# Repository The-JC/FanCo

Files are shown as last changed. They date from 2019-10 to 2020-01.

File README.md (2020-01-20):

# FanCo
  
FanCo is an advanced wind tunnel fan controller. Monitoring and regulating up to 120 fans individually with its custom UI or the API. 
The UI navigation is simple and intuitive utilizing just a rotary encoder.
FanCo is also capable of logging fan speeds over a longer period for later analyzation. 

FanCo is made up of two fundamental components. The master managing the UI and logging. And second, the slave, measuring actual speeds and compensate fluctuations in speed. Each Slave is capable of regulating up to 4 fans. Further slaves can be connected via cables to expand the maximum amounts of fans and also remove the number of control cables needed. 

## Table of contents
- [Requirements](#Requirements)
- [Installation](#Installation)
- [Usage](#Usage)
- [Principle of operation](#Principle%20of%20operation)
- [Troubleshooting](#Troubleshooting)
- [ToDo](#ToDo)

## Requirements
- RaspberryPi Zero (W) or 1 (2 or later only works with custom build)
- Slave PCB manufactured and soldered from your favorite Chinese manufacturer (see [Parts List](/circuits/slave/bom.pdf)).
- USBasp programmer (An Arduino can be used as a programmer).
- Any HDMI compatible display (we used a small 5" HDMI display)
- A rotary encoder as an input
- One or more 4-pin fans
- A 5V power supply to provide power to the Raspberry Pi and the Display

## Installation
### I. RaspberryPi  
1. Download the latest Raspbian Version from https://www.raspberrypi.org/downloads/ and flash it to the SD card.
2. Insert SD card into the pi. Start it check if it boots.
3. Run ```sudo apt-get update & upgrade ``` to update all packages.
4. Make sure you've downloaded and installed pigpiod from http://abyz.me.uk/rpi/pigpio/download.html.
5. Download the latest version of FanCoUI from  
https://github.com/The-JC/Rflw/releases/latest
    > You can use ```wget``` to directly download the binary to the RaspberryPi.
6. To run the FanCo UI run ```./fanco``` in the installation directory.
7. When using an 800x480 display change or add the following lines in  
**/boot/config.txt**
    ```
    hdmi_group=2
    hdmi_mode=87
    hdmi_cvt=800 480 60 0 0 0
    ```
8. To autostart FanCoUI at boot. Add the following lines to your rc.local before the exit 0 line.
```sudo nano /etc/rc.local```
    ```
    pigpiod
    PATH_TO_FANCO/fanco
    ```

### II. Slave
> **Requirments**  
>You will need [avrdude](http://www.nongnu.org/avrdude/) for flashing the program to the Slaves.
>Also you will need avr-gcc installed to compile the program.
>Further the build system CMake and make is required.
>You can install both on Ubuntu or Debian by running ```sudo apt-get install avrdude gcc-avr```
1. Connect the programmer and the slave, like shown in the following picture
![Connection](/docs/images/programming.svg)
2. Connect the programmer to the computer.
3. Change your current directory to ```cd programs/slave/FanRegulator_v01```
4. Change the slave address line ```#define ADDRESS 0xXX``` in ```include/config.h``` starting with 0x04
5. Configure the build by running ```cmake -B build .``` in the root directory of *FanRegulator_v01*
6. Go to the build directory by running ```cd build```
7. Run the following command to compile the program and flash it to the microcontroller: ```make flash```
8. Repeat the previous steps for every other microcontroller only changing the I2C address.

>**NOTE:** Currently only a USBasp programmer is the supported. We´re are working on supporting other programmer types like ArduinoISP. If you can't wait, you could also flash the binaries manualy using avrdude.

### III. Cabling
- Connect the rotary encoder, slave(s) and the display to the Raspberry Pi following the below scheme.
![Cabling](/docs/images/cabling.svg)

## Usage
1. Run ```sudo pigpiod```
2. Start program by running ```./fanco```

## Principle of operation
The slave counts pulses(n) received on the tacho pin in a set interval(dt). By calculating f=n/dt you`ll get the frequency(f) of the input signal. Further multiplication x60 converts the frequency from 1/t in s to min which equals RPMs (revolutions per minute).
Previously calculated speed is used for fine-tuning the fans set signal, to achieve a steady and constant speed at the desired speed.  
Further, the acquired data is requested by the master (RaspberyPi) every second. For logging, displaying and synchronization purposes.  
Firstly it´s averaged out to compensate for measurement and transmission errors. It later gets stored for logging and plotting purposes.

![Schema](/docs/images/schema.svg)

## Troubleshooting
#### Rotary Encoder is not recognized
- Check if cables are connected correctly
- Make sure you have pull-up resistors on all 3 data lines

#### FanCoUI shows invalid or random data
- Make sure all slaves are powered up
- Check the data bus for wiring errors
- Check if all slaves are recognized by running ```i2cdetect -y 1```
- Try running ```i2cdump -y -r 0-2 1 0x04 c```
    - Reading devices fails -> restart all slaves & try updating slaves
    - Reads X X X as byte-value -> restart all slaves
    - Reads some byte-value -> all should be good try updating FanCoUI to the latest version.

## ToDo
- Interval programming
- Extended logs
- Remote control API
- init.d start script
- Enclosure
- Flow dependent speed control

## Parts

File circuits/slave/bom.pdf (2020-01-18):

Qty | Value | Package | Parts | Description
1 | - | 2POL254 | X1 | PHOENIX CONNECTOR
1 | - | M_DIN8 | X8 | 8-Pin Mini-DIN
1 | 100k | R0805 | R16 | RESISTOR, European symbol
4 | 100n | C0805 | C1, C2, C3, C4 | CAPACITOR, European symbol
10 | 10k | R0805 | R1, R2, R3, R4, R5, R6, R7, R8, R9, R10 | RESISTOR, European symbol
5 | 1k | R0805 | R11, R12, R13, R14, R15 | RESISTOR, European symbol
1 | 53047-03 | 53047-03 | X3 | CONNECTOR
5 | 53047-06 | 53047-06 | X2, X4, X5, X6, X7 | CONNECTOR
4 | ATTINY85-20S | SOIC8_EIAJ_208MIL | U1, U2, U3, U4 | ATMEL ATtiny 85
1 | BSS84 | SOT23 | Q2 | P-CHANNEL MOS FET

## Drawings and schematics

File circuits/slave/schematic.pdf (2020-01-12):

A

A

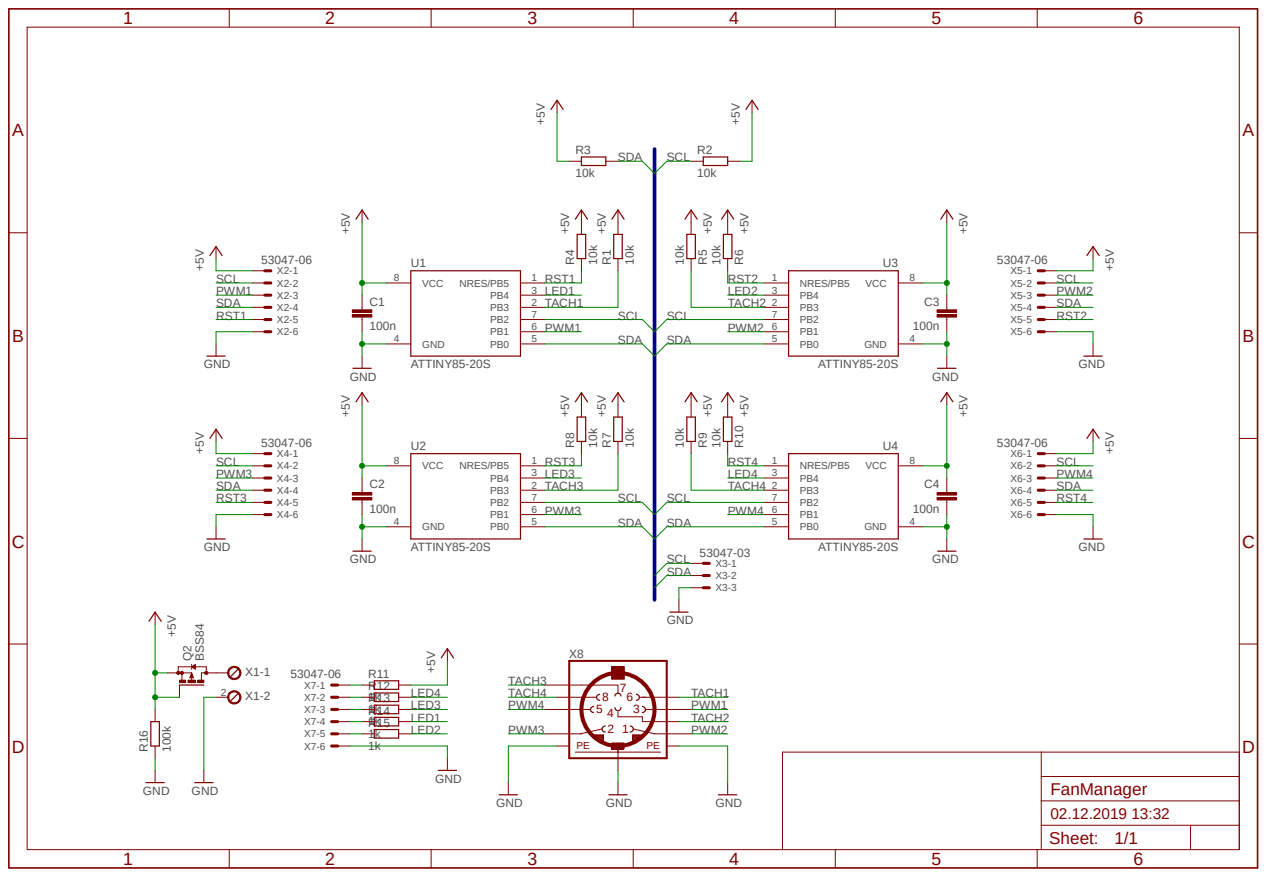
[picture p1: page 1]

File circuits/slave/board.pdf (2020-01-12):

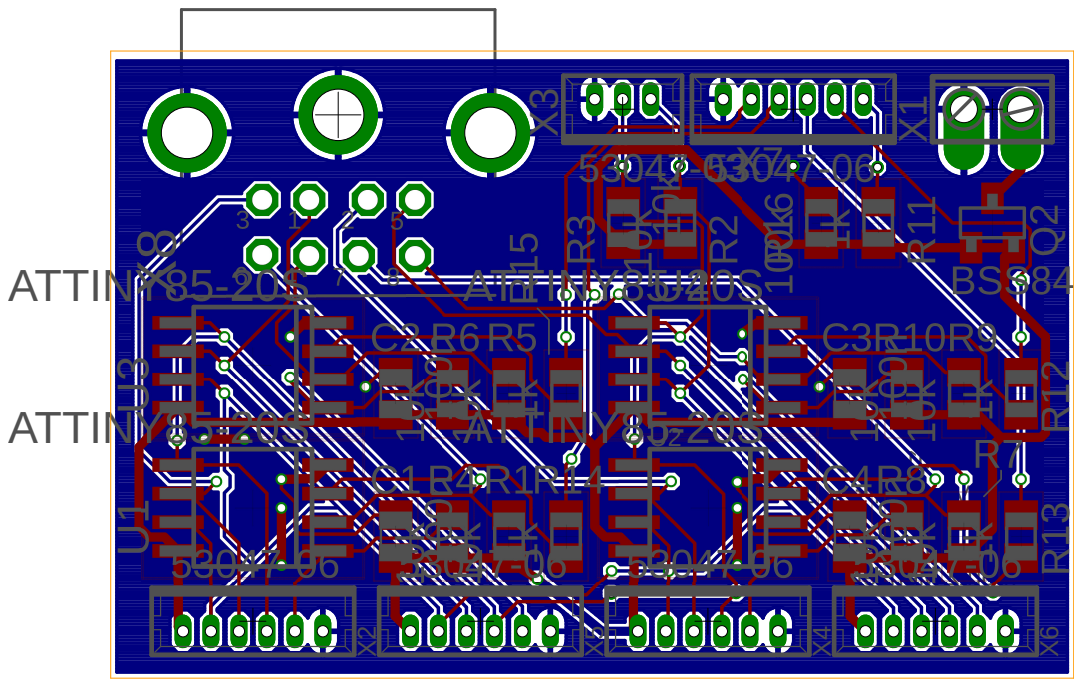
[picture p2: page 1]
ATTINY85-20S

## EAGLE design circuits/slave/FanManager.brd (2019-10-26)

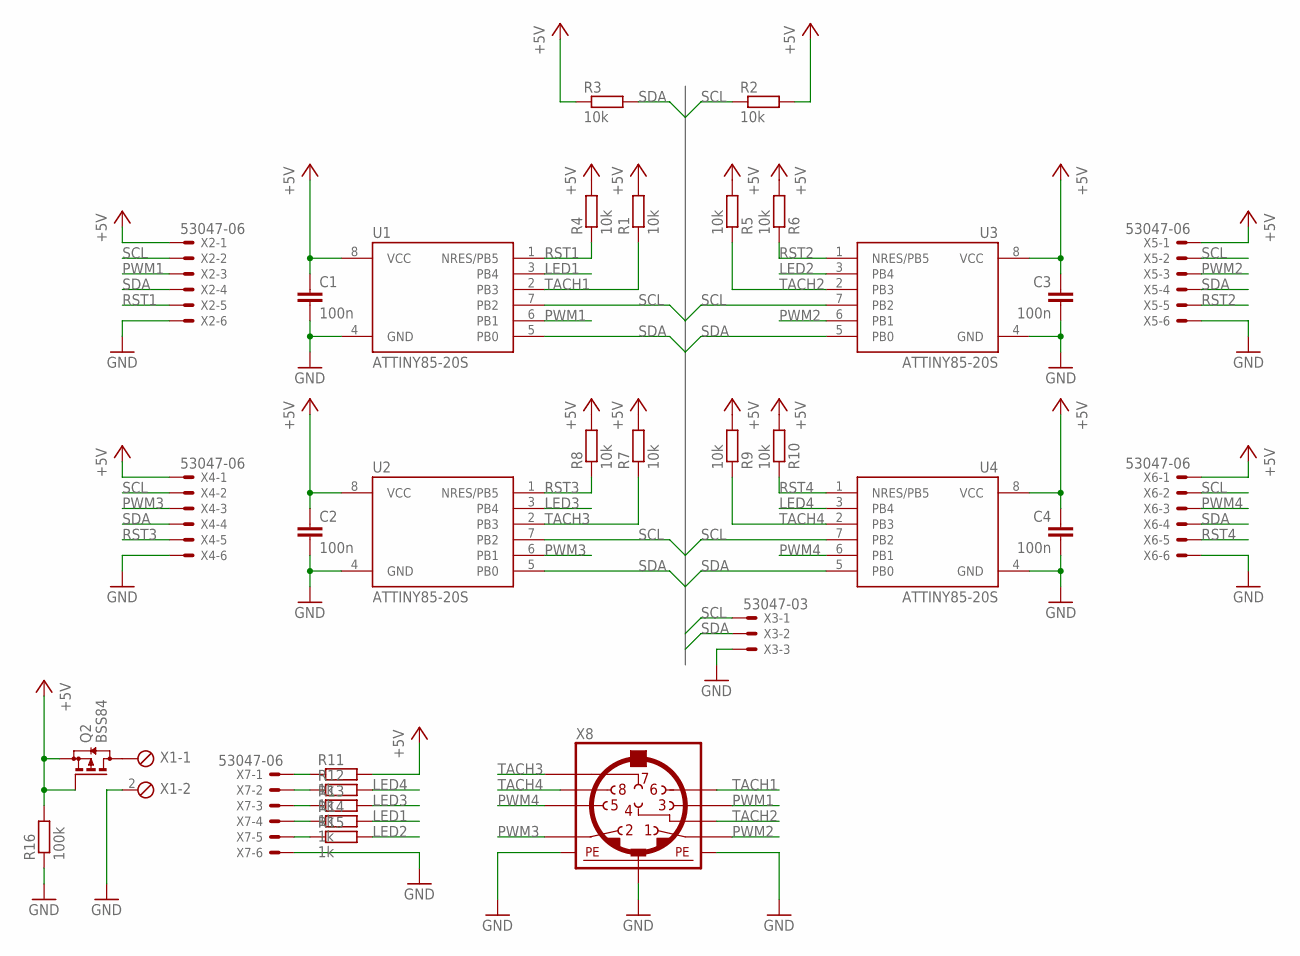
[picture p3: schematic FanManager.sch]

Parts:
C1, C2, C3, C4: 100n; C0805
Q2: BSS84; SOT23
R1, R2, R3, R4, R5, R6, R7, R8, R9, R10: 10k; R0805
R11, R12, R13, R14, R15: 1k; R0805
R16: 100k; R0805
U1, U2, U3, U4: ATTINY85-20S; SOIC8_EIAJ_208MIL
X1: KLEMME_2XRAND_LANGPAD; 2POL254
X2, X4, X5, X6, X7: 53047-06
X3: 53047-03
X8: MINI_DIN_8; M_DIN8

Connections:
+5V: C1.1, C2.1, C3.1, C4.1, Q2.1 (G), Q2.2 (S), R1.2, R2.2, R3.1, R4.2, R5.2, R6.2, R7.2, R8.2, R9.2, R10.2, R11.2, R16.2, U1.8 (VCC), U2.8 (VCC), U3.8 (VCC), U4.8 (VCC), X2.1, X4.1, X5.1, X6.1
GND: C1.2, C2.2, C3.2, C4.2, R16.1, U1.4 (GND), U2.4 (GND), U3.4 (GND), U4.4 (GND), X1.2, X2.6, X3.3, X4.6, X5.6, X6.6, X7.6, X8.SH1 (PE1), X8.SH2 (PE2), X8.SH3 (PE3)
LED1: R14.2, U1.3 (PB4)
LED2: R15.2, U3.3 (PB4)
LED3: R13.2, U2.3 (PB4)
LED4: R12.2, U4.3 (PB4)
unnamed: Q2.3 (D), X1.1
unnamed: R11.1, X7.1
unnamed: R12.1, X7.2
unnamed: R13.1, X7.3
unnamed: R14.1, X7.4
unnamed: R15.1, X7.5
PWM1: U1.6 (PB1), X2.3, X8.3
PWM2: U3.6 (PB1), X5.3, X8.1
PWM3: U2.6 (PB1), X4.3, X8.2
PWM4: U4.6 (PB1), X6.3, X8.5
RST1: R4.1, U1.1 (NRES/PB5), X2.5
RST2: R6.1, U3.1 (NRES/PB5), X5.5
RST3: R8.1, U2.1 (NRES/PB5), X4.5
RST4: R10.1, U4.1 (NRES/PB5), X6.5
SCL: R2.1, U1.7 (PB2), U2.7 (PB2), U3.7 (PB2), U4.7 (PB2), X2.2, X3.1, X4.2, X5.2, X6.2
SDA: R3.2, U1.5 (PB0), U2.5 (PB0), U3.5 (PB0), U4.5 (PB0), X2.4, X3.2, X4.4, X5.4, X6.4
TACH1: R1.1, U1.2 (PB3), X8.6
TACH2: R5.1, U3.2 (PB3), X8.4
TACH3: R7.1, U2.2 (PB3), X8.7
TACH4: R9.1, U4.2 (PB3), X8.8

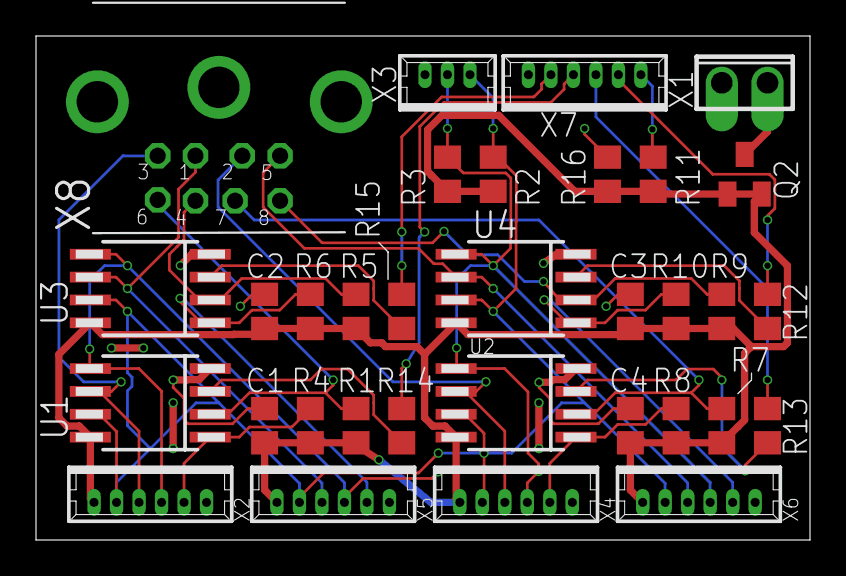
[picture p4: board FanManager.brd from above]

Board: 2 copper layers, 43.0 x 28.0 mm, 33 parts (0 on the bottom side), 26 nets.

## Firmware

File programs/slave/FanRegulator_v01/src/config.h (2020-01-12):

/*
 * config.h
 *
 *  Tim Breuer september 2019
 */ 

#ifndef CONFIG_H_
#define CONFIG_H_

//adress
#define ADRESS 0x04

//pwm
#define PWM_FREQUENCY 10000

//fan specific
#define COUNTS_PER_ROTATION 3
#define MAX_SPEED 12000

//calculation speed in sec
#define REFRESH_SPEED 1

//pid values
#define KP 0.7
#define KI 0.5
#define KD 0.0
#define DEVIATION 100

//do not change
#define F_CPU 1000000
#define PWM_PRESCALER 1
#define TACHO_PIN 3

#endif /* CONFIG_H_ */

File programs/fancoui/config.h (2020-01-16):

#ifndef CONFIG_H
#define CONFIG_H
#pragma once

#include <string>

#define FANS 18
#define PLOTLEN 120	// s

#define MAXSPEED 12000 // RPMs

#define SHORT_PRESS_TIME 500	// ms
#define LONG_PRESS_TIME 1000*10 // ms

const uint8_t addresses[FANS] = { 0x04, 0x05, 0x06, 0x07 };

#define GPIOHOST "localhost";
#define GPIOPORT "8888";

#endif // CONFIG_H

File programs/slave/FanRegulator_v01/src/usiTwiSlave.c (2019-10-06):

/********************************************************************************

USI TWI Slave driver.

Created by Donald R. Blake. donblake at worldnet.att.net
Adapted by Jochen Toppe, jochen.toppe at jtoee.com

---------------------------------------------------------------------------------

Created from Atmel source files for Application Note AVR312: Using the USI Module
as an I2C slave.

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
---------------------------------------------------------------------------------

Change Activity:

    Date       Description
   ------      -------------
  16 Mar 2007  Created.
  27 Mar 2007  Added support for ATtiny261, 461 and 861.
  26 Apr 2007  Fixed ACK of slave address on a read.
  04 Jul 2007  Fixed USISIF in ATtiny45 def
  12 Dev 2009  Added callback functions for data requests
  06 Feb 2015  Minor change to allow mutli-byte requestFrom() from master.
  10 Feb 2015  Simplied RX/TX buffer code and allowed use of full buffer.
  12 Dec 2016  Added support for ATtiny167

********************************************************************************/


/********************************************************************************
                                    includes
********************************************************************************/

#include <avr/io.h>
#include <avr/interrupt.h>

#include "usiTwiSlave.h"
//#include "../common/util.h"


/********************************************************************************
                            device dependent defines
********************************************************************************/

#if defined( __AVR_ATtiny167__ )
#  define DDR_USI             DDRB
#  define PORT_USI            PORTB
#  define PIN_USI             PINB
#  define PORT_USI_SDA        PB0
#  define PORT_USI_SCL        PB2
#  define PIN_USI_SDA         PINB0
#  define PIN_USI_SCL         PINB2
#  define USI_START_COND_INT  USISIF
#  define USI_START_VECTOR    USI_START_vect
#  define USI_OVERFLOW_VECTOR USI_OVERFLOW_vect
#endif

#if defined( __AVR_ATtiny2313__ )
#  define DDR_USI             DDRB
#  define PORT_USI            PORTB
#  define PIN_USI             PINB
#  define PORT_USI_SDA        PB5
#  define PORT_USI_SCL        PB7
#  define PIN_USI_SDA         PINB5
#  define PIN_USI_SCL         PINB7
#  define USI_START_COND_INT  USISIF
#  define USI_START_VECTOR    USI_START_vect
#  define USI_OVERFLOW_VECTOR USI_OVERFLOW_vect
#endif

#if defined(__AVR_ATtiny84__) | \
     defined(__AVR_ATtiny44__)
#  define DDR_USI             DDRA
#  define PORT_USI            PORTA
#  define PIN_USI             PINA
#  define PORT_USI_SDA        PORTA6
#  define PORT_USI_SCL        PORTA4
#  define PIN_USI_SDA         PINA6
#  define PIN_USI_SCL         PINA4
#  define USI_START_COND_INT  USISIF
#  define USI_START_VECTOR    USI_START_vect
#  define USI_OVERFLOW_VECTOR USI_OVF_vect
#endif

#if defined( __AVR_ATtiny25__ ) | \
     defined( __AVR_ATtiny45__ ) | \
     defined( __AVR_ATtiny85__ )
#  define DDR_USI             DDRB
#  define PORT_USI            PORTB
#  define PIN_USI             PINB
#  define PORT_USI_SDA        PB0
#  define PORT_USI_SCL        PB2
#  define PIN_USI_SDA         PINB0
#  define PIN_USI_SCL         PINB2
#  define USI_START_COND_INT  USISIF
#  define USI_START_VECTOR    USI_START_vect
#  define USI_OVERFLOW_VECTOR USI_OVF_vect
#endif

#if defined( __AVR_ATtiny26__ )
#  define DDR_USI             DDRB
#  define PORT_USI            PORTB
#  define PIN_USI             PINB
#  define PORT_USI_SDA        PB0
#  define PORT_USI_SCL        PB2
#  define PIN_USI_SDA         PINB0
#  define PIN_USI_SCL         PINB2
#  define USI_START_COND_INT  USISIF
#  define USI_START_VECTOR    USI_STRT_vect
#  define USI_OVERFLOW_VECTOR USI_OVF_vect
#endif

#if defined( __AVR_ATtiny261__ ) | \
      defined( __AVR_ATtiny461__ ) | \
      defined( __AVR_ATtiny861__ )
#  define DDR_USI             DDRB
#  define PORT_USI            PORTB
#  define PIN_USI             PINB
#  define PORT_USI_SDA        PB0
#  define PORT_USI_SCL        PB2
#  define PIN_USI_SDA         PINB0
#  define PIN_USI_SCL         PINB2
#  define USI_START_COND_INT  USISIF
#  define USI_START_VECTOR    USI_START_vect
#  define USI_OVERFLOW_VECTOR USI_OVF_vect
#endif

#if defined( __AVR_ATmega165__ ) | \
     defined( __AVR_ATmega325__ ) | \
     defined( __AVR_ATmega3250__ ) | \
     defined( __AVR_ATmega645__ ) | \
     defined( __AVR_ATmega6450__ ) | \
     defined( __AVR_ATmega329__ ) | \
     defined( __AVR_ATmega3290__ )
#  define DDR_USI             DDRE
#  define PORT_USI            PORTE
#  define PIN_USI             PINE
#  define PORT_USI_SDA        PE5
#  define PORT_USI_SCL        PE4
#  define PIN_USI_SDA         PINE5
#  define PIN_USI_SCL         PINE4
#  define USI_START_COND_INT  USISIF
#  define USI_START_VECTOR    USI_START_vect
#  define USI_OVERFLOW_VECTOR USI_OVERFLOW_vect
#endif

#if defined( __AVR_ATmega169__ )
#  define DDR_USI             DDRE
#  define PORT_USI            PORTE
#  define PIN_USI             PINE
#  define PORT_USI_SDA        PE5
#  define PORT_USI_SCL        PE4
#  define PIN_USI_SDA         PINE5
#  define PIN_USI_SCL         PINE4
#  define USI_START_COND_INT  USISIF
#  define USI_START_VECTOR    USI_START_vect
#  define USI_OVERFLOW_VECTOR USI_OVERFLOW_vect
#endif



/********************************************************************************

                        functions implemented as macros

********************************************************************************/

#define SET_USI_TO_SEND_ACK( ) \
{ \
  /* prepare ACK */ \
  USIDR = 0; \
  /* set SDA as output */ \
  DDR_USI |= ( 1 << PORT_USI_SDA ); \
  /* clear all interrupt flags, except Start Cond */ \
  USISR = \
       ( 0 << USI_START_COND_INT ) | \
       ( 1 << USIOIF ) | ( 1 << USIPF ) | \
       ( 1 << USIDC )| \
       /* set USI counter to shift 1 bit */ \
       ( 0x0E << USICNT0 ); \
}

#define SET_USI_TO_READ_ACK( ) \
{ \
  /* set SDA as input */ \
  DDR_USI &= ~( 1 << PORT_USI_SDA ); \
  /* prepare ACK */ \
  USIDR = 0; \
  /* clear all interrupt flags, except Start Cond */ \
  USISR = \
       ( 0 << USI_START_COND_INT ) | \
       ( 1 << USIOIF ) | \
       ( 1 << USIPF ) | \
       ( 1 << USIDC ) | \
       /* set USI counter to shift 1 bit */ \
       ( 0x0E << USICNT0 ); \
}

#define SET_USI_TO_TWI_START_CONDITION_MODE( ) \
{ \
  USICR = \
       /* enable Start Condition Interrupt, disable Overflow Interrupt */ \
       ( 1 << USISIE ) | ( 0 << USIOIE ) | \
       /* set USI in Two-wire mode, no USI Counter overflow hold */ \
       ( 1 << USIWM1 ) | ( 0 << USIWM0 ) | \
       /* Shift Register Clock Source = External, positive edge */ \
       /* 4-Bit Counter Source = external, both edges */ \
       ( 1 << USICS1 ) | ( 0 << USICS0 ) | ( 0 << USICLK ) | \
       /* no toggle clock-port pin */ \
       ( 0 << USITC ); \
  USISR = \
        /* clear all interrupt flags, except Start Cond */ \
        ( 0 << USI_START_COND_INT ) | ( 1 << USIOIF ) | ( 1 << USIPF ) | \
        ( 1 << USIDC ) | ( 0x0 << USICNT0 ); \
}

#define SET_USI_TO_SEND_DATA( ) \
{ \
  /* set SDA as output */ \
  DDR_USI |=  ( 1 << PORT_USI_SDA ); \
  /* clear all interrupt flags, except Start Cond */ \
  USISR    =  \
       ( 0 << USI_START_COND_INT ) | ( 1 << USIOIF ) | ( 1 << USIPF ) | \
       ( 1 << USIDC) | \
       /* set USI to shift out 8 bits */ \
       ( 0x0 << USICNT0 ); \
}

#define SET_USI_TO_READ_DATA( ) \
{ \
  /* set SDA as input */ \
  DDR_USI &= ~( 1 << PORT_USI_SDA ); \
  /* clear all interrupt flags, except Start Cond */ \
  USISR    = \
       ( 0 << USI_START_COND_INT ) | ( 1 << USIOIF ) | \
       ( 1 << USIPF ) | ( 1 << USIDC ) | \
       /* set USI to shift out 8 bits */ \
       ( 0x0 << USICNT0 ); \
}

#define USI_RECEIVE_CALLBACK() \
{ \
    if (usi_onReceiverPtr) \
    { \
        if (usiTwiAmountDataInReceiveBuffer()) \
        { \
            usi_onReceiverPtr(usiTwiAmountDataInReceiveBuffer()); \
        } \
    } \
}

#define ONSTOP_USI_RECEIVE_CALLBACK() \
{ \
    if (USISR & ( 1 << USIPF )) \
    { \
        USI_RECEIVE_CALLBACK(); \
    } \
}


#define USI_REQUEST_CALLBACK() \
{ \
    USI_RECEIVE_CALLBACK(); \
    if(usi_onRequestPtr) usi_onRequestPtr(); \
}

/********************************************************************************

                                   typedef's

********************************************************************************/

typedef enum
{
  USI_SLAVE_CHECK_ADDRESS                = 0x00,
  USI_SLAVE_SEND_DATA                    = 0x01,
  USI_SLAVE_REQUEST_REPLY_FROM_SEND_DATA = 0x02,
  USI_SLAVE_CHECK_REPLY_FROM_SEND_DATA   = 0x03,
  USI_SLAVE_REQUEST_DATA                 = 0x04,
  USI_SLAVE_GET_DATA_AND_SEND_ACK        = 0x05
} overflowState_t;



/********************************************************************************

                                local variables

********************************************************************************/

static uint8_t                  slaveAddress;
static volatile overflowState_t overflowState;


static uint8_t          rxBuf[ TWI_RX_BUFFER_SIZE ];
static volatile uint8_t rxHead;
static volatile uint8_t rxTail;
static volatile uint8_t rxCount;

static uint8_t          txBuf[ TWI_TX_BUFFER_SIZE ];
static volatile uint8_t txHead;
static volatile uint8_t txTail;
static volatile uint8_t txCount;



/********************************************************************************

                                local functions

********************************************************************************/



// flushes the TWI buffers

static
void
flushTwiBuffers(
  void
)
{
  rxTail = 0;
  rxHead = 0;
  rxCount = 0;
  txTail = 0;
  txHead = 0;
  txCount = 0;
} // end flushTwiBuffers



/********************************************************************************

                                public functions

********************************************************************************/



// initialise USI for TWI slave mode

void
TinyWireS_stop_check(
void
)
{
	if (!usi_onReceiverPtr)
	{
		// no onReceive callback, nothing to do...
		return;
	}
	if (!(USISR & ( 1 << USIPF )))
	{
		// Stop not detected
		return;
	}
	uint8_t amount = usiTwiAmountDataInReceiveBuffer();
	if (amount == 0)
	{
		// no data in buffer
		return;
	}
	usi_onReceiverPtr(amount);
}

void
usiTwiSlaveInit(
  uint8_t ownAddress
)
{

  flushTwiBuffers( );

  slaveAddress = ownAddress;

  // In Two Wire mode (USIWM1, USIWM0 = 1X), the slave USI will pull SCL
  // low when a start condition is detected or a counter overflow (only
  // for USIWM1, USIWM0 = 11).  This inserts a wait state.  SCL is released
  // by the ISRs (USI_START_vect and USI_OVERFLOW_vect).

  // Set SCL and SDA as output
  DDR_USI |= ( 1 << PORT_USI_SCL ) | ( 1 << PORT_USI_SDA );

  // set SCL high
  PORT_USI |= ( 1 << PORT_USI_SCL );

  // set SDA high
  PORT_USI |= ( 1 << PORT_USI_SDA );

  // Set SDA as input
  DDR_USI &= ~( 1 << PORT_USI_SDA );

  USICR =
       // enable Start Condition Interrupt
       ( 1 << USISIE ) |
       // disable Overflow Interrupt
       ( 0 << USIOIE ) |
       // set USI in Two-wire mode, no USI Counter overflow hold
       ( 1 << USIWM1 ) | ( 0 << USIWM0 ) |
       // Shift Register Clock Source = external, positive edge
       // 4-Bit Counter Source = external, both edges
       ( 1 << USICS1 ) | ( 0 << USICS0 ) | ( 0 << USICLK ) |
       // no toggle clock-port pin
       ( 0 << USITC );

  // clear all interrupt flags and reset overflow counter

  USISR = ( 1 << USI_START_COND_INT ) | ( 1 << USIOIF ) | ( 1 << USIPF ) | ( 1 << USIDC );

} // end usiTwiSlaveInit


bool usiTwiDataInTransmitBuffer(void)
{

  // return 0 (false) if the receive buffer is empty
  return txCount;

} // end usiTwiDataInTransmitBuffer


// put data in the transmission buffer, wait if buffer is full
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

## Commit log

2019-10-26 added circuits and step_response program and assorted these
    [FanManager.brd, FanManager.sch]
2020-01-08 Schematic and board PDF

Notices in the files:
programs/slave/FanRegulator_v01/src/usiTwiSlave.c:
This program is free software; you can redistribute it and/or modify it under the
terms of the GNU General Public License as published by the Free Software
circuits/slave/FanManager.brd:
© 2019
